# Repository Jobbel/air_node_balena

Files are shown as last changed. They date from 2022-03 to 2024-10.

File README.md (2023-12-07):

# air_node
 Software package and hardware for a BalenaOS based air quality sensor node featuring cellular networking, 
 MQTT, GPS localisation, local USB drive data logging and support for the following sensors:
 
 - Alphasense OPC-N3 PM Sensor
 - 2xADS1115 connected to NO-B4,CO-B4,OX-B431,NO2-B43 Alphasense ISBs
 - HYT221 Temperature/Humidity Sensor
 - SHT3x Temperature/Humidity Sensor

Hardware used during developement:

 - Raspberry Pi 4
 - SIM7600 4G Modem/GPS receiver
 - USB Stick for local data storage (needs to be vfat formatted)

Configuration can be done via BalenaCloud environment variables or in src/config_cloudless.py if no cloud will be used.

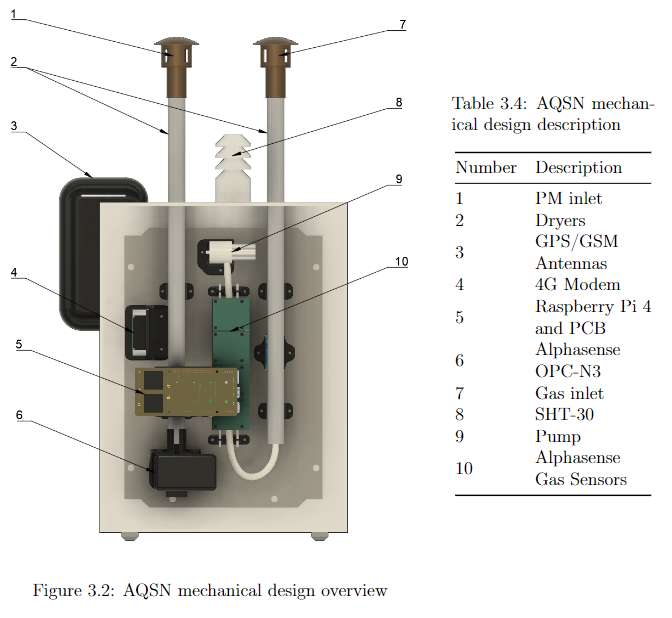
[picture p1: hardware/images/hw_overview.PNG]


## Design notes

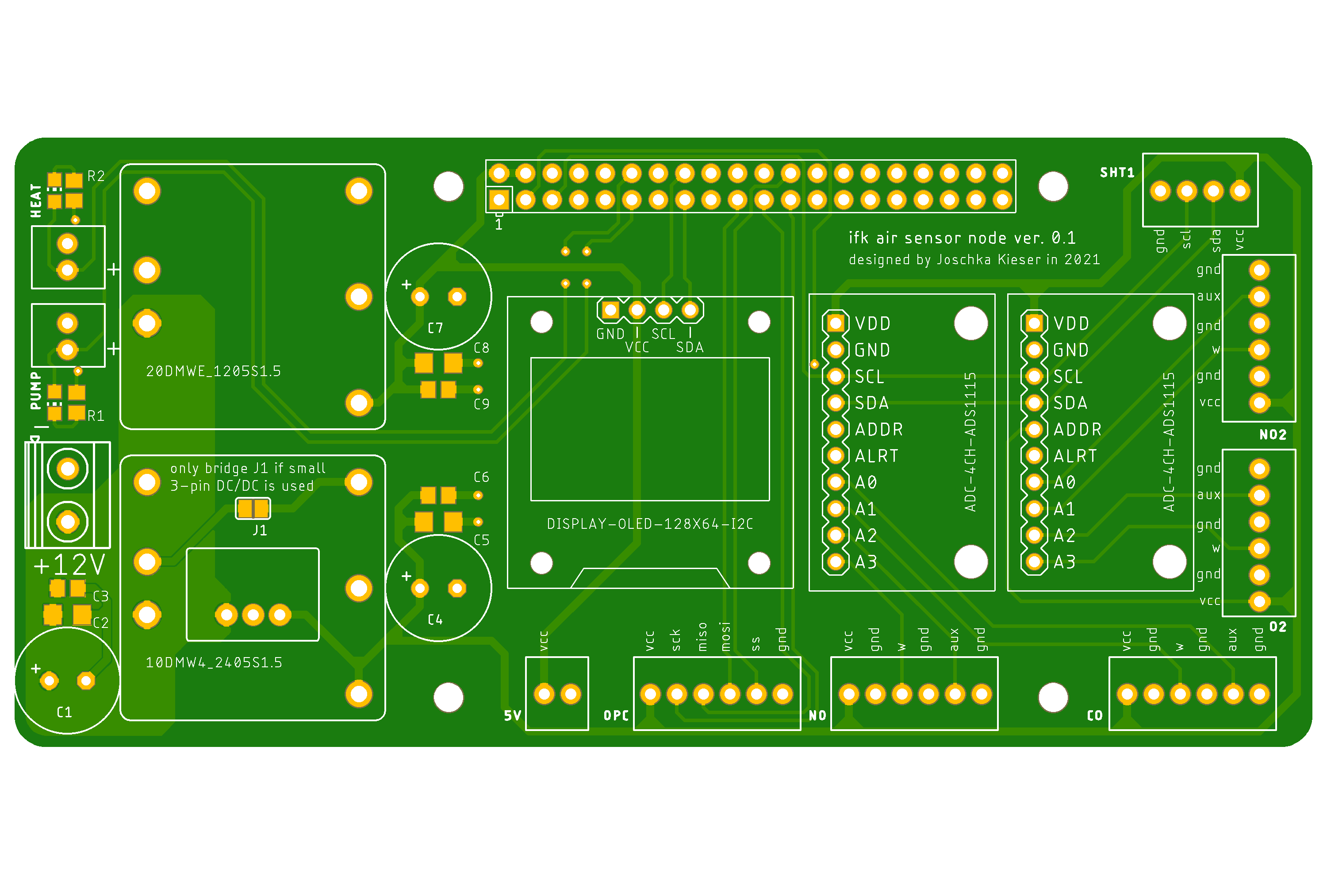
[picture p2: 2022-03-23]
hardware/pcb_files/air_node.png

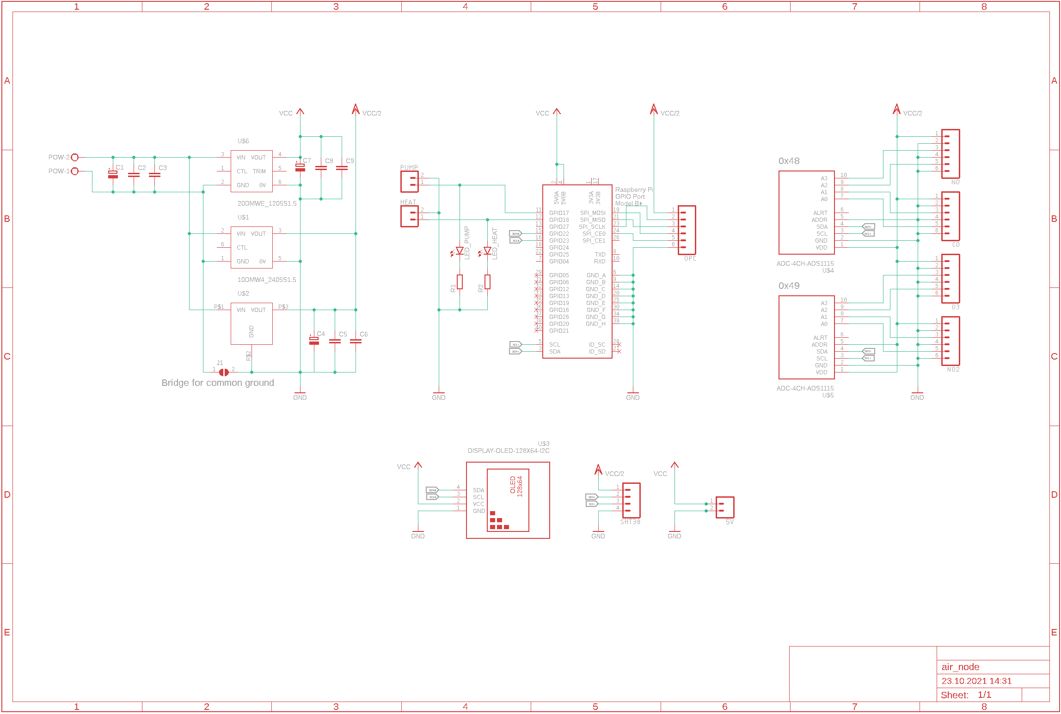
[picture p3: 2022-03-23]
hardware/pcb_files/schematic.png

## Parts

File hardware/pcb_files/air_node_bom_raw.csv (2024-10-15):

Qty | Value | Device | Package | Parts | Description
7 |  | C-EUC0805 | C0805 | C3, C6, C9, C10, C11, C12, C13 | CAPACITOR, European symbol
3 |  | C-EUC1206 | C1206 | C2, C5, C8 | CAPACITOR, European symbol
8 |  | CONN_021X02_NO_SILK | 1X02_NO_SILK | 5V, A0, A1, A2, A3, HEAT, PUMP, USB-DISCONNECTOR | Multi connection point. Often used as Generic Header-pin footprint for 0.1 inch spaced/style header connections
1 |  | CONN_031X03_NO_SILK | 1X03_NO_SILK | 1-WIRE | Multi connection point. Often used as Generic Header-pin footprint for 0.1 inch spaced/style header connections
2 |  | CONN_041X04_NO_SILK | 1X04_NO_SILK | SHT30, UART | Multi connection point. Often used as Generic Header-pin footprint for 0.1 inch spaced/style header connections
5 |  | CONN_06NO_SILK_FEMALE_PTH | 1X06_NO_SILK | CO, NO, NO2, O3, OPC | Multi connection point. Often used as Generic Header-pin footprint for 0.1 inch spaced/style header connections
3 |  | CPOL-EUE3.5-10 | E3,5-10 | C1, C4, C7 | POLARIZED CAPACITOR, European symbol
3 |  | LEDCHIP-LED0805 | CHIP-LED0805 | LED_DISCO, LED_HEAT, LED_PUMP | LED
8 |  | R-EU_R0805 | R0805 | R1, R2, R3, R4, R5, R6, R7, R8 | RESISTOR, European symbol
1 |  | SJ | SJ | J1 | SMD solder JUMPER
1 | 10DMW4_2405S1.5 | 10DMW4_2405S1.5 | 10DMW4_2405S1.5 | U$1
1 | 20DMWE_1205S1.5 | 20DMWE_1205S1.5 | 20DMWE_1205S1.5 | U$6
3 | ADC-4CH-ADS1115 | ADC-4CH-ADS1115 | ADC-4CH-ADS1115 | U$4, U$5, U$7 | 4 Channel 16-Bit Analog-to-Digital Converter based on ADS1115 chip
1 | DISPLAY-OLED-128X64-I2C | DISPLAY-OLED-128X64-I2C | DISPLAY-OLED-128X64-I2C | U$3 | 128x64 Dot Matrix OLED Module based on SSD1306 chip
1 | LME78_05-1.0 | LME78_05-1.0 | LME78_05-1.0 | U$2
1 | MKDSN1,5/2-5,08 | MKDSN1,5/2-5,08 | MKDSN1,5/2-5,08 | POW | MKDSN 1,5/ 2-5,08 Printklemme
1 | RASPI_BOARD_B+#_E4 | RASPI_BOARD_B+#_E4 | RASPI_BOARD_B+_EDGES_4DRILL | X1 | Raspberry Pi GPIO connector with markings for the outer dimensions of the Raspberry Pi board model B+

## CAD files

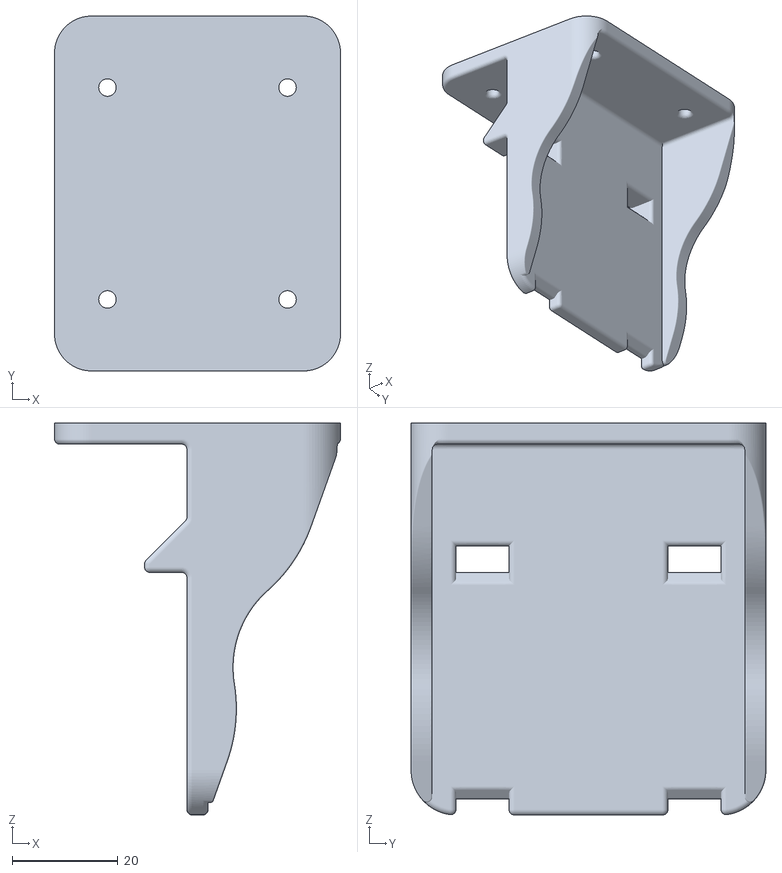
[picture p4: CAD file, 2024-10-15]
hardware/stl_files/modem_holder_ngff.stl
54.0 x 67.0 x 74.0

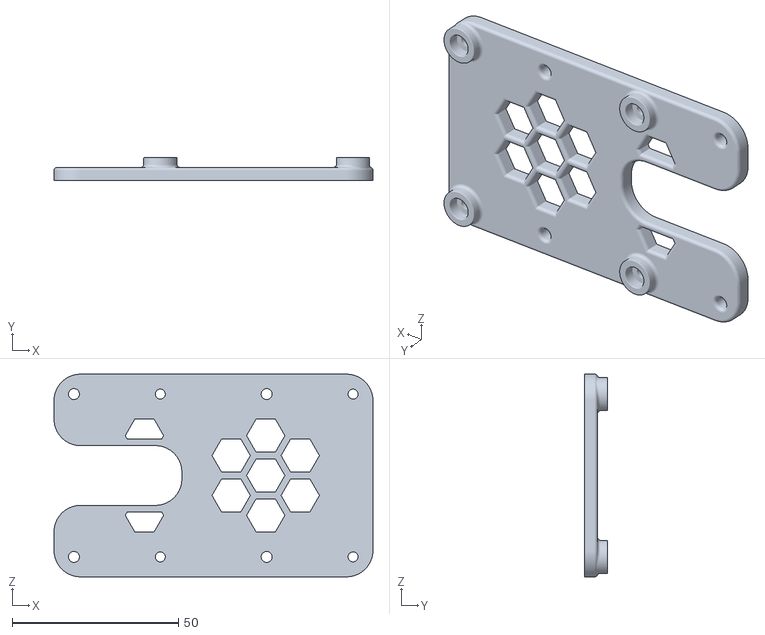
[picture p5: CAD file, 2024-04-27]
hardware/stl_files/pi_holder_V2_1cm_right_shifted.stl
96.0 x 7.00 x 61.0

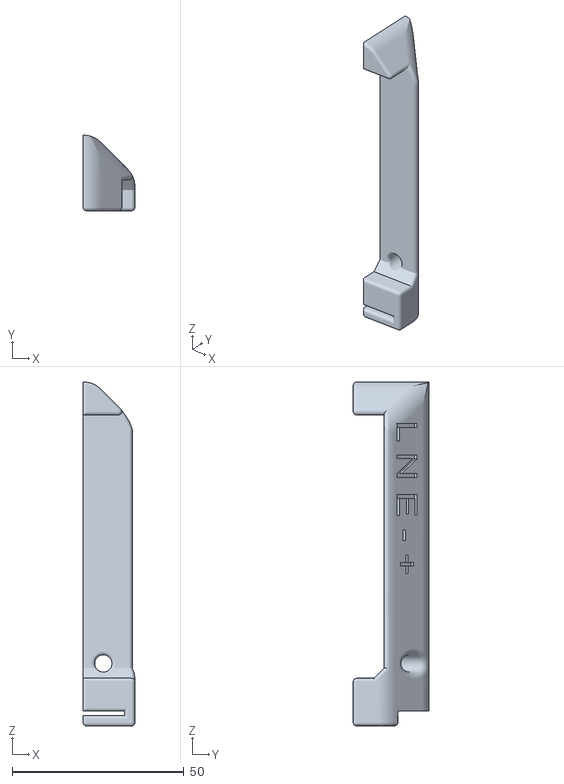
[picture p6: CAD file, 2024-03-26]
hardware/stl_files/netzteil_abdeckung.stl
15.1 x 22.0 x 100.1

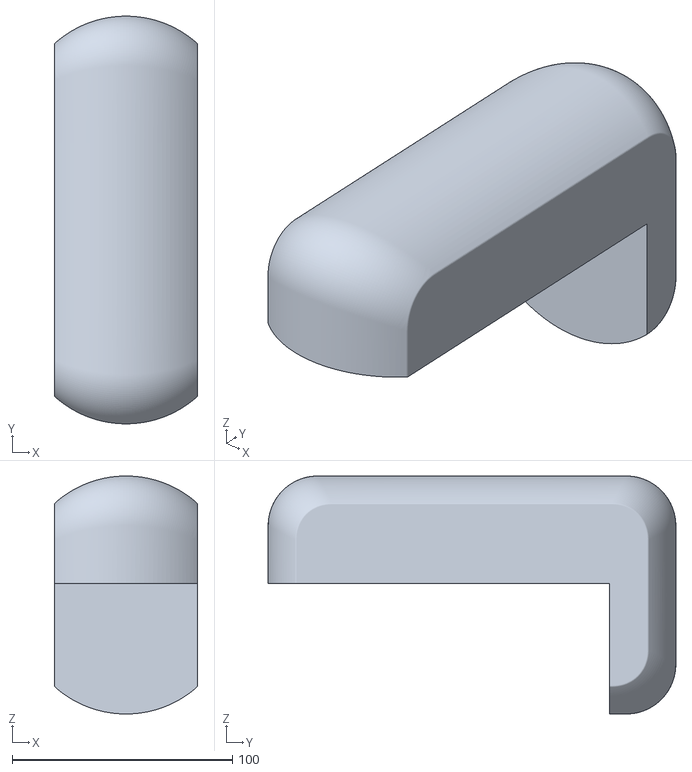
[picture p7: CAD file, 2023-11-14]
hardware/stl_files/antennendeckung_bopla_mod_easier_to_print_alternative.stl
65.0 x 185.0 x 108.0

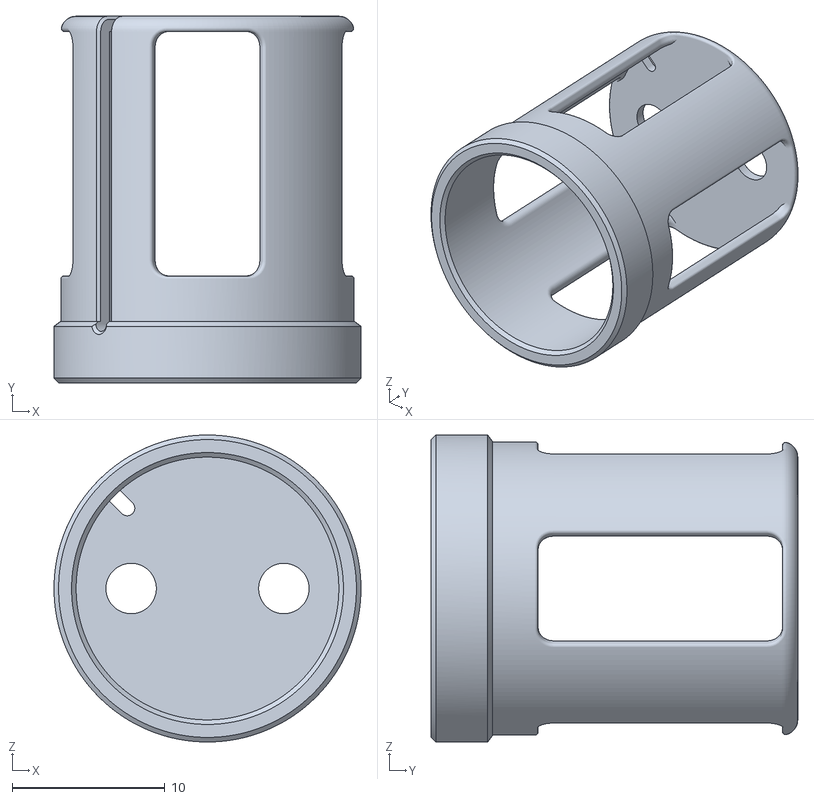
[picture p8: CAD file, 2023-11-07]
hardware/stl_files/grid_mount.stl
20.1 x 24.0 x 20.1

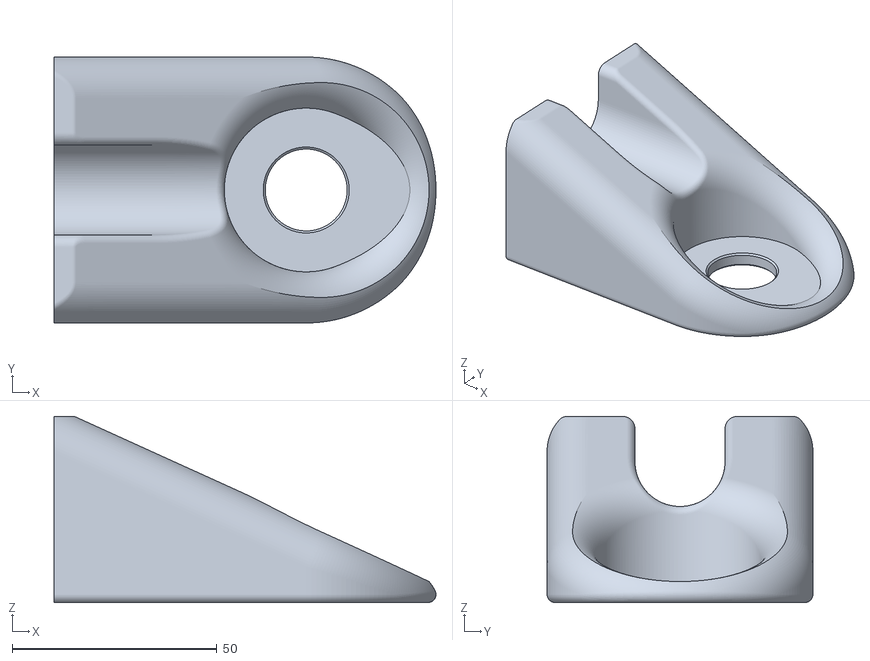
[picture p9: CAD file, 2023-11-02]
hardware/stl_files/humidhalter.stl
93.4 x 65.0 x 45.5

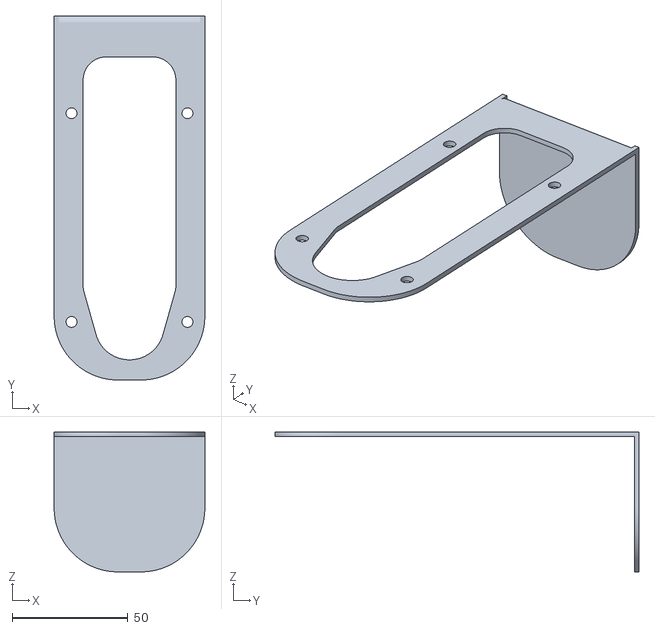
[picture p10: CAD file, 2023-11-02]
hardware/stl_files/antennenabdeckung_bopla_mod_guide.stl
65.0 x 157.0 x 60.3

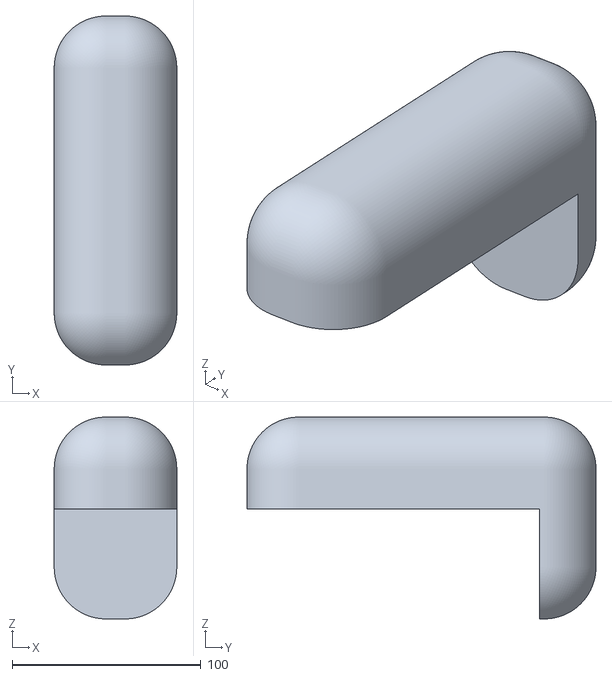
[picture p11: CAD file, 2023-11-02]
hardware/stl_files/antennendeckung_bopla_mod.stl
65.0 x 185.0 x 107.0

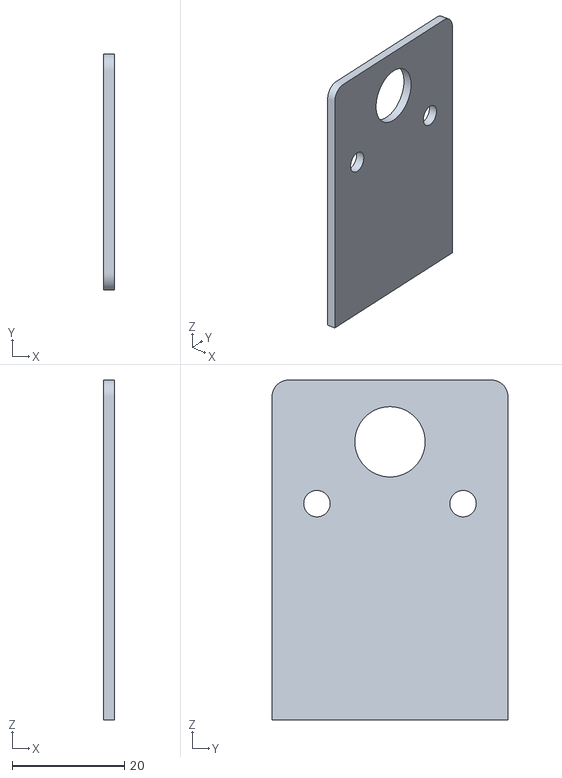
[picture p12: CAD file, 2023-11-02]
hardware/stl_files/humidhalter_guide.stl
2.00 x 42.0 x 60.5

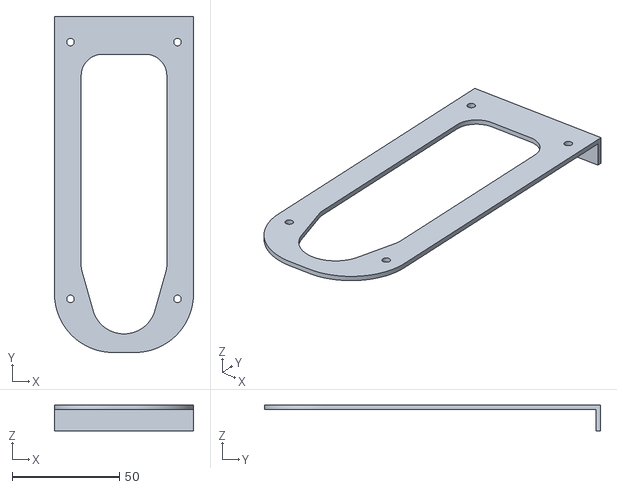
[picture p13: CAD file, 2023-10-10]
hardware/stl_files/antennenabdeckung_guide.stl
65.0 x 157.0 x 12.0

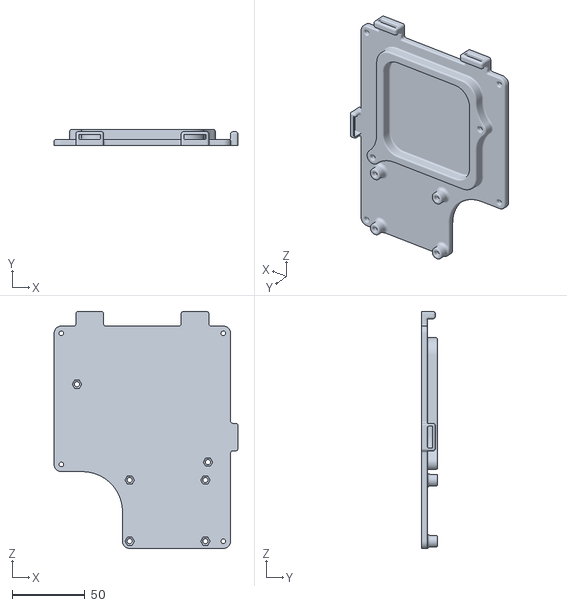
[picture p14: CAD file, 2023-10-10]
hardware/stl_files/netzteilhalter_oben.stl
126.3 x 11.0 x 162.8

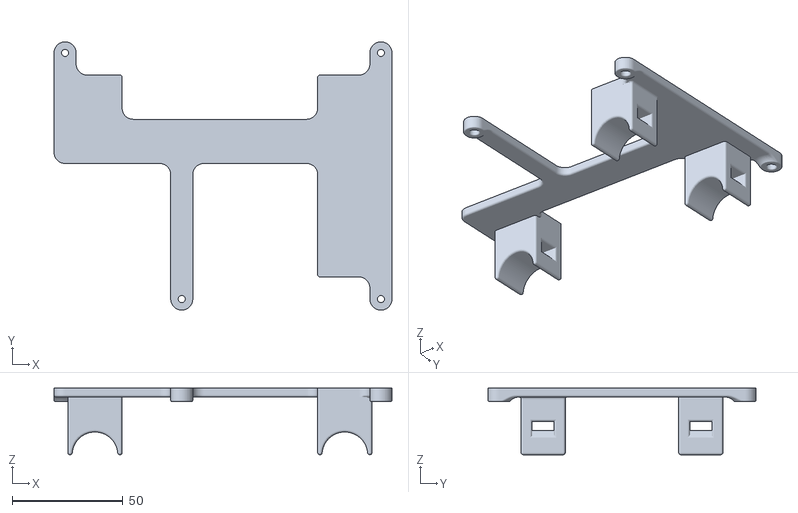
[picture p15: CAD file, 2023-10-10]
hardware/stl_files/netzteilhalter_unten.stl
152.8 x 121.3 x 30.1

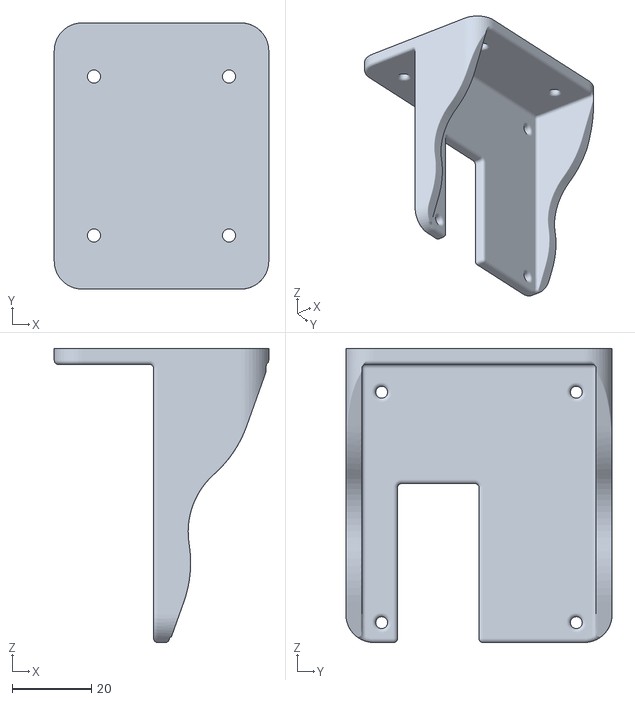
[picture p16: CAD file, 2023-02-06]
hardware/stl_files/modem_round_V2.stl
54.0 x 67.0 x 74.0

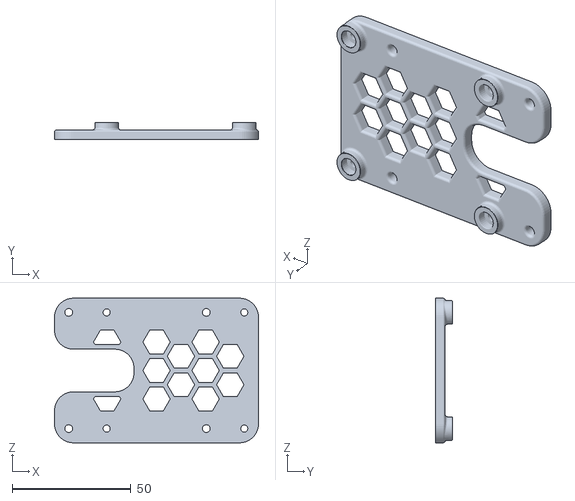
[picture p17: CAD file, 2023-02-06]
hardware/stl_files/pi_holder_V2.stl
86.0 x 7.00 x 61.0

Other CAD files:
hardware/stl_files/gas.stl
hardware/stl_files/hat.stl
hardware/stl_files/pump.stl
hardware/stl_files/heat.stl
hardware/stl_files/antennendeckung.stl
hardware/stl_files/bottom.stl
hardware/stl_files/dcdc.stl
hardware/stl_files/guide.stl
hardware/stl_files/humidhat.stl
hardware/stl_files/middle.stl
hardware/stl_files/modem.stl
hardware/stl_files/modem_round.stl
hardware/stl_files/netzteil_halter_groß.stl
hardware/stl_files/opc.stl
hardware/stl_files/opcadapter.stl
hardware/stl_files/pi.stl
hardware/stl_files/pi_holder.stl
hardware/stl_files/pump_alt.stl

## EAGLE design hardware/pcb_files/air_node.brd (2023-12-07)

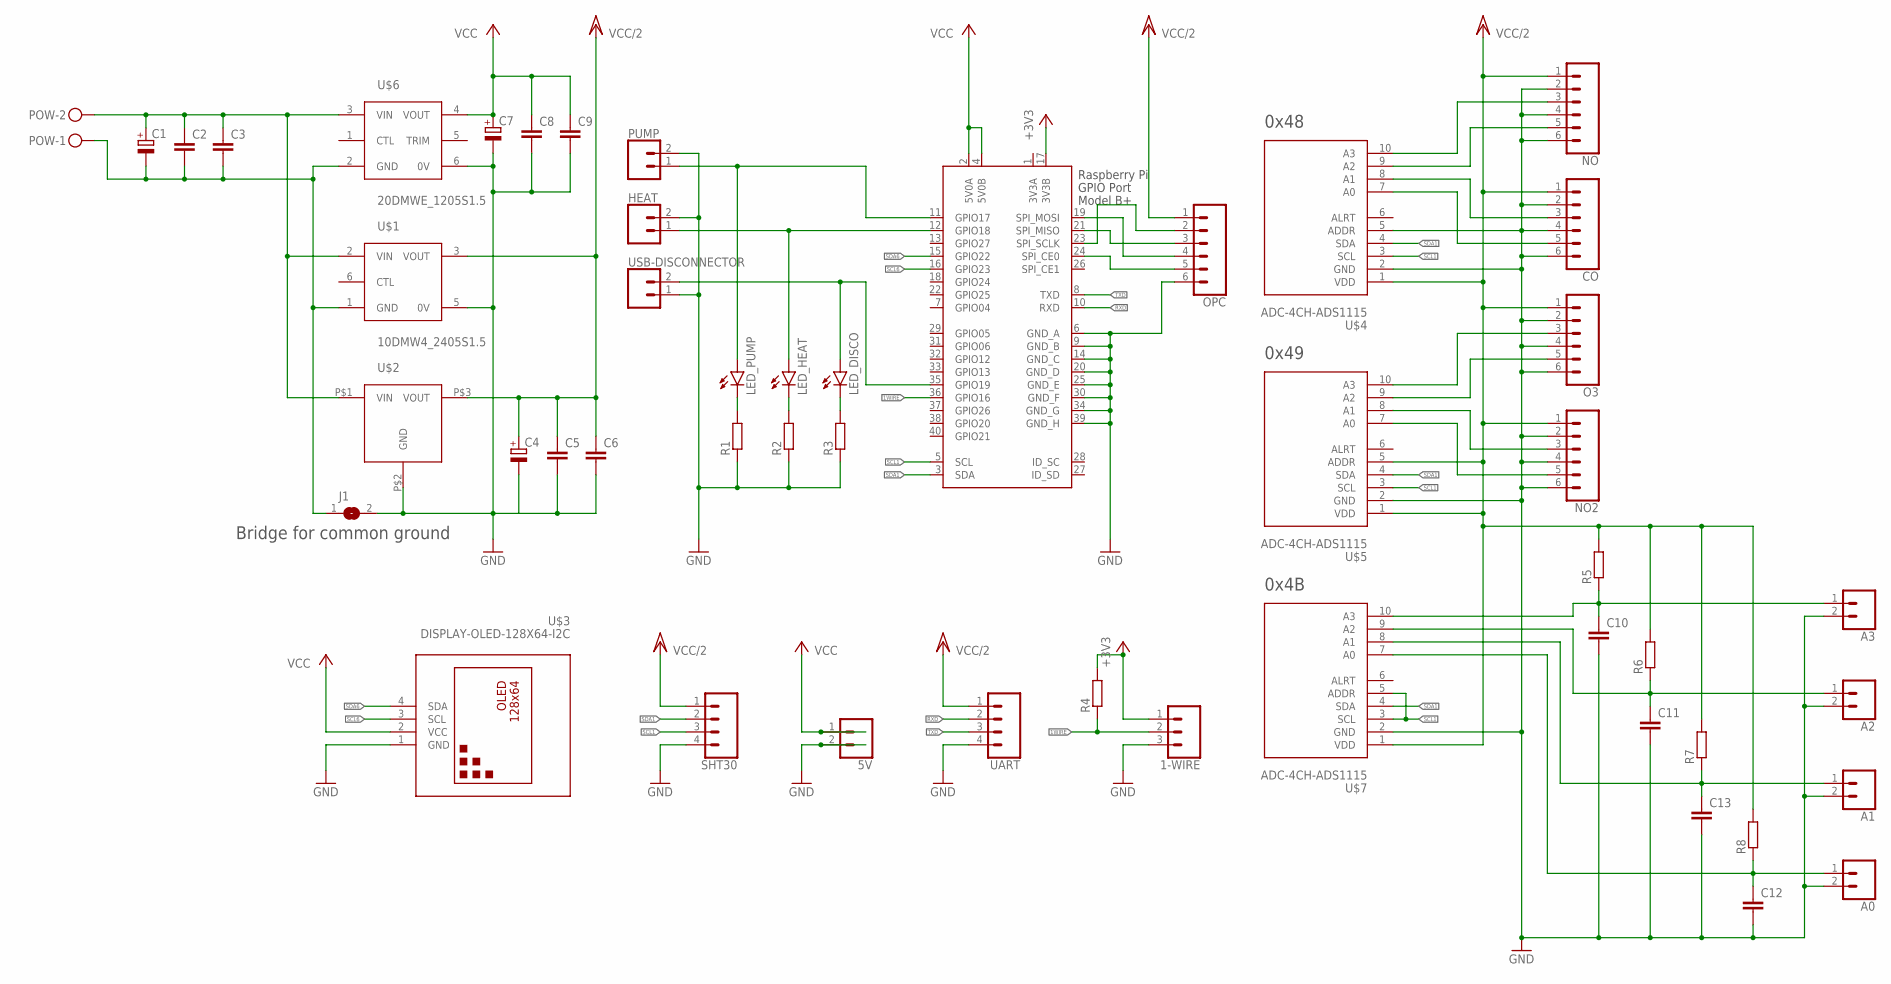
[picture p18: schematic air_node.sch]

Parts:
1-WIRE: CONN_031X03_NO_SILK; 1X03_NO_SILK
5V: CONN_021X02_NO_SILK; 1X02_NO_SILK
A0, A1, A2, A3: CONN_021X02_NO_SILK; 1X02_NO_SILK
C1, C4, C7: CPOL-EUE3.5-10; E3,5-10
C2, C5, C8: C-EUC1206; C1206
C3, C6, C9, C10, C11, C12, C13: C-EUC0805; C0805
CO: CONN_06NO_SILK_FEMALE_PTH; 1X06_NO_SILK
HEAT: CONN_021X02_NO_SILK; 1X02_NO_SILK
J1: SJ
LED_DISCO: LEDCHIP-LED0805; CHIP-LED0805
LED_HEAT: LEDCHIP-LED0805; CHIP-LED0805
LED_PUMP: LEDCHIP-LED0805; CHIP-LED0805
NO, NO2: CONN_06NO_SILK_FEMALE_PTH; 1X06_NO_SILK
O3: CONN_06NO_SILK_FEMALE_PTH; 1X06_NO_SILK
OPC: CONN_06NO_SILK_FEMALE_PTH; 1X06_NO_SILK
POW: MKDSN1,5/2-5,08
PUMP: CONN_021X02_NO_SILK; 1X02_NO_SILK
R1, R2, R3, R4, R5, R6, R7, R8: R-EU_R0805; R0805
SHT30: CONN_041X04_NO_SILK; 1X04_NO_SILK
U$1: 10DMW4_2405S1.5
U$2: LME78_05-1.0
U$3: DISPLAY-OLED-128X64-I2C
U$4, U$5, U$7: ADC-4CH-ADS1115
U$6: 20DMWE_1205S1.5
UART: CONN_041X04_NO_SILK; 1X04_NO_SILK
USB-DISCONNECTOR: CONN_021X02_NO_SILK; 1X02_NO_SILK
X1: RASPI_BOARD_B+#_E4; RASPI_BOARD_B+_EDGES_4DRILL

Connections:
1WIRE: 1-WIRE.2, R4.1, X1.36 (GPIO16)
3V3A: X1.1 (3V3A)
12VGND: C1.-, C2.2, C3.2, J1.1, POW.1, U$1.1 (GND), U$6.2 (GND)
+3V3: 1-WIRE.1, R4.2, X1.17 (3V3B)
+12V: C1.+, C2.1, C3.1, POW.2, U$1.2 (VIN), U$2.P$1 (VIN), U$6.3 (VIN)
GND: 1-WIRE.3, 5V.2, A0.2, A1.2, A2.2, A3.2, C4.-, C5.2, C6.2, C7.-, C8.2, C9.2, C10.2, C11.2, C12.2, C13.2, CO.2, CO.4, CO.6, HEAT.2, J1.2, NO.2, NO.4, NO.6, NO2.2, NO2.4, NO2.6, O3.2, O3.4, O3.6, OPC.6, PUMP.2, R1.1, R2.1, R3.1, SHT30.4, U$1.5 (0V), U$2.P$2 (GND), U$3.1 (GND), U$4.2 (GND), U$4.5 (ADDR), U$5.2 (GND), U$6.6 (0V), U$7.2 (GND), UART.4, USB-DISCONNECTOR.1, X1.6 (GND_A), X1.9 (GND_B), X1.14 (GND_C), X1.20 (GND_D), X1.25 (GND_E), X1.30 (GND_F), X1.34 (GND_G), X1.39 (GND_H)
unnamed: HEAT.1, LED_HEAT.A, X1.12 (GPIO18)
unnamed: LED_PUMP.A, PUMP.1, X1.11 (GPIO17)
unnamed: OPC.2, X1.23 (SPI_SCLK)
unnamed: OPC.4, X1.19 (SPI_MOSI)
unnamed: OPC.5, X1.24 (SPI_CE0)
unnamed: OPC.3, X1.21 (SPI_MISO)
unnamed: NO.3, U$4.10 (A3)
unnamed: NO.5, U$4.9 (A2)
unnamed: CO.3, U$4.8 (A1)
unnamed: CO.5, U$4.7 (A0)
unnamed: O3.3, U$5.10 (A3)
unnamed: O3.5, U$5.9 (A2)
unnamed: NO2.3, U$5.8 (A1)
unnamed: NO2.5, U$5.7 (A0)
unnamed: LED_PUMP.C, R1.2
unnamed: LED_HEAT.C, R2.2
unnamed: A1.1, C13.1, R7.1, U$7.8 (A1)
unnamed: LED_DISCO.A, USB-DISCONNECTOR.2, X1.35 (GPIO19)
unnamed: A0.1, C12.1, R8.1, U$7.7 (A0)
unnamed: A3.1, C10.1, R5.1, U$7.10 (A3)
unnamed: A2.1, C11.1, R6.1, U$7.9 (A2)
unnamed: LED_DISCO.C, R3.2
RXD: UART.2, X1.10 (RXD)
SCL1: SHT30.3, U$4.3 (SCL), U$5.3 (SCL), U$7.3 (SCL), U$7.5 (ADDR), X1.5 (SCL)
SCL6: U$3.3 (SCL), X1.16 (GPIO23)
SDA1: SHT30.2, U$4.4 (SDA), U$5.4 (SDA), U$7.4 (SDA), X1.3 (SDA)
SDA6: U$3.4 (SDA), X1.15 (GPIO22)
TXD: UART.3, X1.8 (TXD)
VCC: 5V.1, C7.+, C8.1, C9.1, U$3.2 (VCC), U$6.4 (VOUT), X1.2 (5V0A), X1.4 (5V0B)
VCC/2: C4.+, C5.1, C6.1, CO.1, NO.1, NO2.1, O3.1, OPC.1, R5.2, R6.2, R7.2, R8.2, SHT30.1, U$1.3 (VOUT), U$2.P$3 (VOUT), U$4.1 (VDD), U$5.1 (VDD), U$5.5 (ADDR), U$7.1 (VDD), UART.1

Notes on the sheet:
0x49
0x48
Bridge for common ground
0x4B

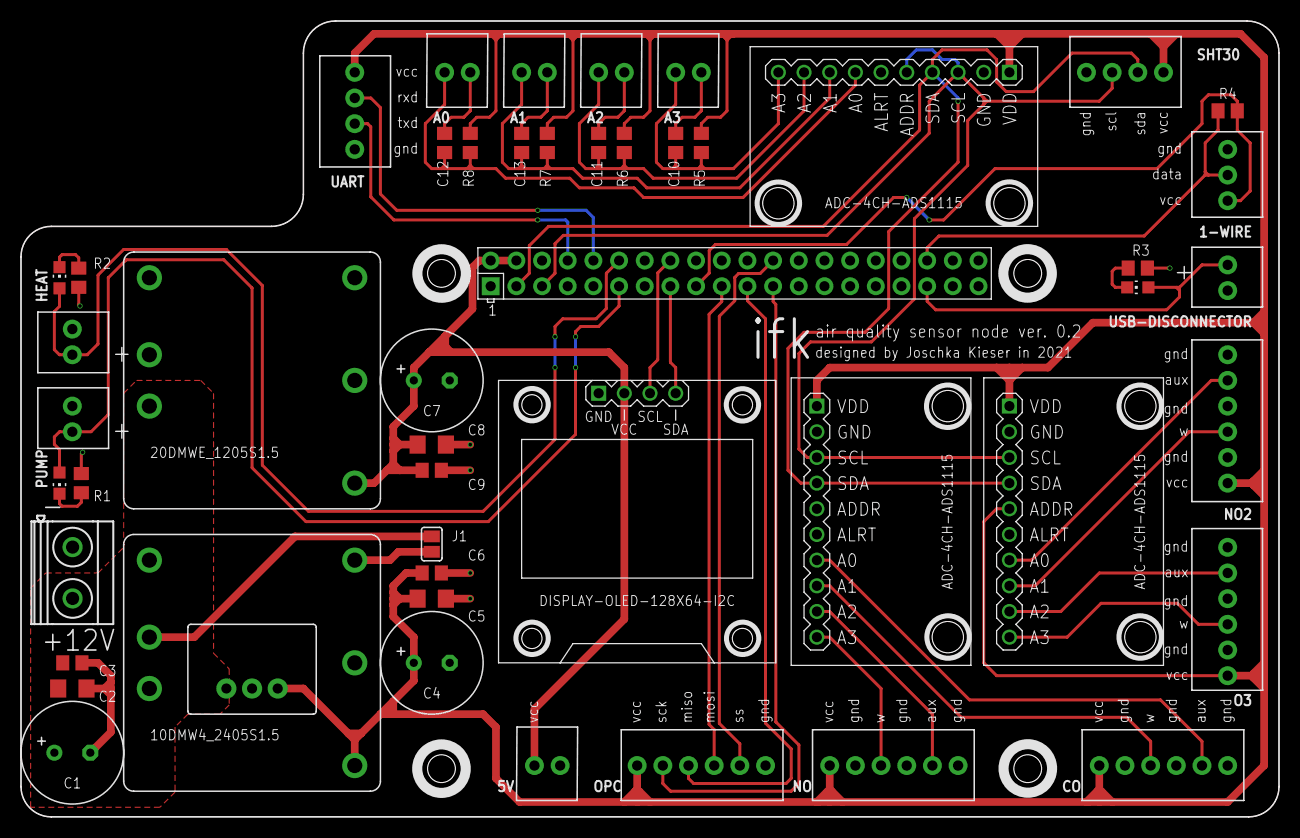
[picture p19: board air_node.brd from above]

Board: 2 copper layers, 124.5 x 78.7 mm, 50 parts (0 on the bottom side), 35 nets.

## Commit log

2021-08-18 added two point calibration to sensors
    all sensors inherit from generic_sensor which implements the two point calibration
2021-08-18 changed calibration
    1,1,1,1 will disable any calibration
2021-08-24 threaded logging
    thread refactor logging and lob config var rename
2021-10-03 modem, exit, overheat
    removed modem fail counter, catching exit signals, added heater safety shutoff
2021-10-23 hardcoded temperature n factor
2022-03-23 added stl files
    [antennendeckung.stl, bottom.stl, dcdc.stl, gas.stl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]
2022-03-23 added more hardware files
    [air_node.brd, air_node.sch, antennendeckung.stl, bottom.stl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]
2023-01-20 ensure disabled sht heater
2023-01-20 added rsync call to logging thread
2023-02-06 updated pi/modem holders
    Added cutouts for sim/sd card accessibility
    [modem_round_V2.stl, pi_holder_V2.stl]
2023-03-08 rsync mount check
2023-03-11 removed fs type from mount
2023-03-11 watchdog init print
2023-03-11 fixed rsync mount check
2023-03-11 added new modem device
2023-03-11 add usb mounted check
2023-07-20 pcb v0.2
    added one-wire, uart, usb disconnector port and one more ads1115
    [air_node.brd, air_node.sch]
2023-07-23 turn off sht heater and oled pi3 dtoverlay comment
2023-07-24 added one wire heater temp sensor
2023-07-30 measure air and heater
2023-08-19 new heater config
2023-08-19 heater controller with polynomial
2023-08-19 auto thermocouple sensor
2023-10-20 adjust modem power pin to hardware v0.2
2023-10-21 fix offline sensors during startup
2023-11-02 added new model stls
    [antennenabdeckung_bopla_mod_guide.stl, antennendeckung_bopla_mod.stl, humidhalter.stl, humidhalter_guide.stl]
2023-11-07 added grid_mount
    [grid_mount.stl]
2024-01-17 add adjustable minimal drying temperature
    Minimal drying temperature to avoid freezing/condensation inside the Container, env var HEATER_MIN_TEMP
2024-03-26 Added PSU cover
    Cover for the exposed terminals of the power supply unit. Requires one heat set insert and M3x10 screw to mount
    [netzteil_abdeckung.stl]
2024-04-27 higher heater shutdown priority
2024-04-27 Added shifted pi holder for small enclosures
    [pi_holder_V2_1cm_right_shifted.stl]
2024-10-15 some hardware files, generated bom and centroid file
    [air_node_bom_raw.csv, air_node_centroid.csv]
2024-10-15 new zip tie modem mount
    [modem_holder_ngff.stl]
2024-11-05 use correct type for min heater temp
2025-03-17 heating pid power limit
2025-03-18 modem reset before power cycle

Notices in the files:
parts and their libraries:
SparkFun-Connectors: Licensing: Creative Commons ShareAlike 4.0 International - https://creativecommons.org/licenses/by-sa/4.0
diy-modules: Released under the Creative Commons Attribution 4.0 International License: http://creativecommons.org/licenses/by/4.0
